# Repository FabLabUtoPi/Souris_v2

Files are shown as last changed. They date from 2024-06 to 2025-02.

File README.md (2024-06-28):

# Souris_v2
Evolution du prototype de souris - Lauréat ANCT
Suite à la réalisation et mis en test des premiers prototypes de la [souris réalisée par le FabLab UtoPi](https://github.com/FabLabUtoPi/Souris) 
Les évolutions suivantes ont été retenues après analyse des retours des utilisateurs/testeurs  

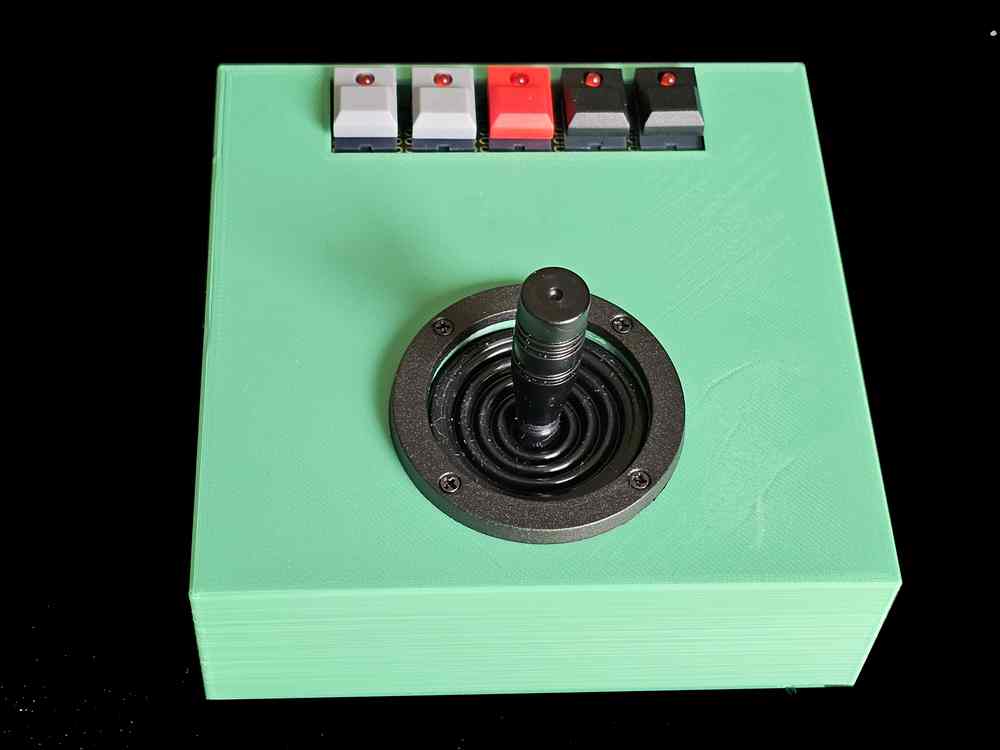
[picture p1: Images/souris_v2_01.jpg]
Image de la souris dans sa deuxième version : boîtier un peu plus grand et joystick analogique.


## Evolutions par rapport au prototype

### Taille du boîtier 
Lors des manipulations du joystick il arrive quel le boîtier se soulève
Deux approches sont possibles : Alourdir le boîtier ou augmenter sa taille 
Le manque de stabilité semble du à la taille du boîtier, la solution retenue  été d'augmenter légèrement la taille du boîtier en conservant le format carré de départ.

### Sensibilité du joystick
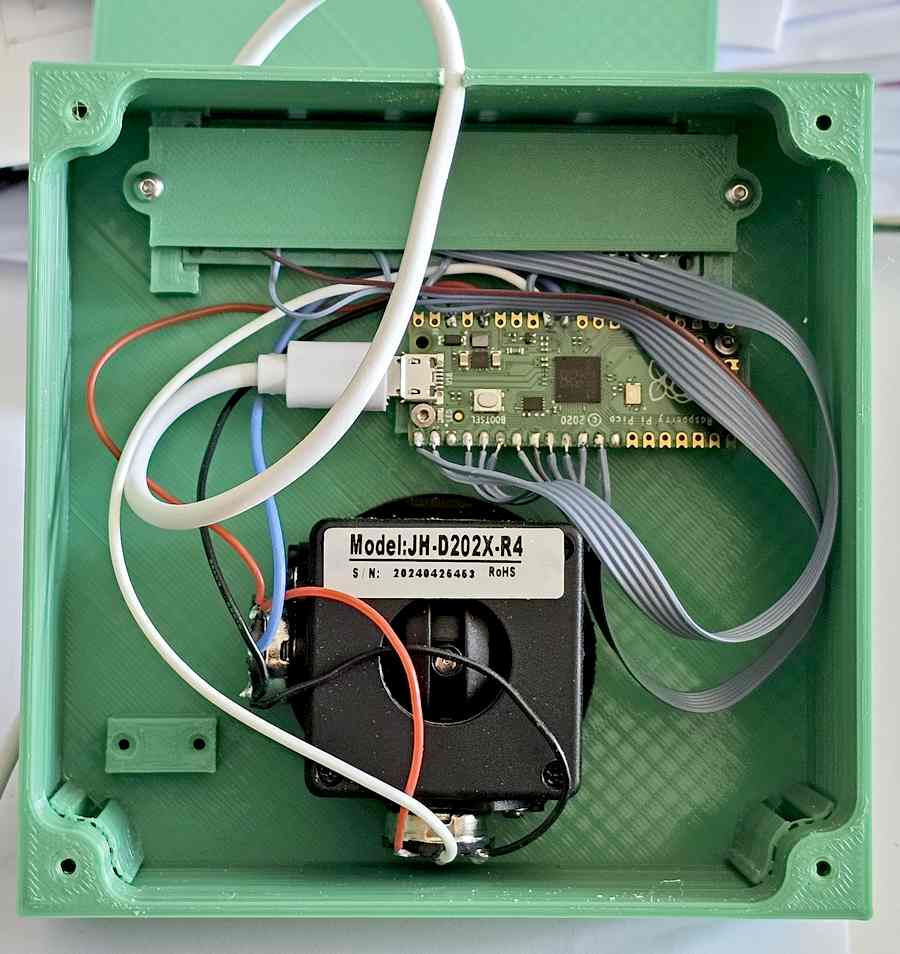
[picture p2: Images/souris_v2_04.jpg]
Image de l'intérieur de la souris dans sa deuxième version : boîtier un peu plus grand et joystick analogique.
  
Le joystick retenu à l'origine est un joystick digital. Les directions de déplacement du curseur de la souris sont commandées par des switchs (des interrupteurs) qui sont activés lorsque l'utilisateur pousse le levier dans une direction. L'accélération de déplacement du curseur est obtenue en maintenant le leviier poussé pendant au moins 0,5 seconde. Si l'utilisateur relache le levier ou change de direction, le déplacement revient en vitesse lente. Il faut de nouveau 0,5 seconde pour accélérer le déplacement. Ceci a conduit à adopter un joystick analogique. le déplacement du levier modifie une tension. En fonction de la position du levier la tension est plus ou moins élevée. Il est possible de définir dans le programme les seuils pour lesquels on passe de la vitesse lente à la vitesse rapide. L'utilisataur peut ainsi doser le déplacement du curseur instantanément, sans devoir respecter un délai.

### Filtrage des mouvements involontaires
La souris peut être utilisée par des personnes présentant des mouvements involontaires (~Parkinson). le joystick analogique permet de filtrer ces mouvements involontaires en filtrant les mouvements pour utiliser une valeur moyenne. 

### Adaptation de la préhension
Le joystick permet de monter un système de préhension adapté à la personne (boule, repose poignet, poignée adaptée après scan de la main)
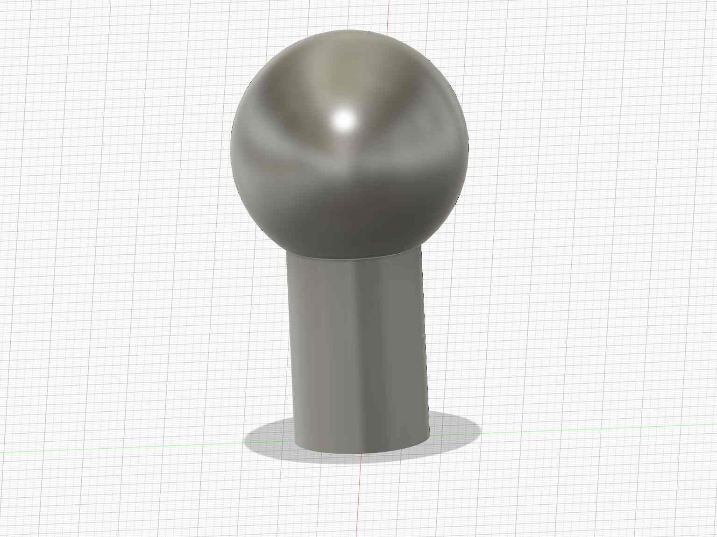
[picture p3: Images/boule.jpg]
Image d'un boule adaptée au joystick analogique.

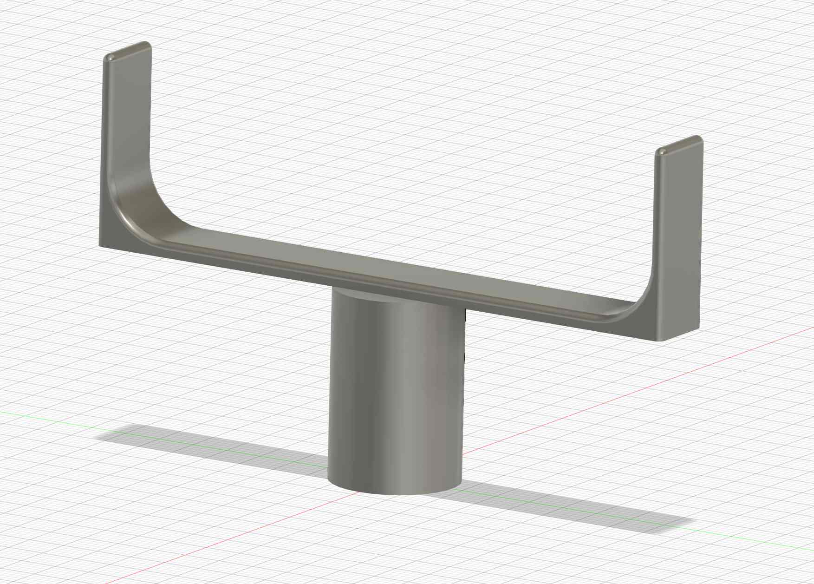
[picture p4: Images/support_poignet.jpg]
Image d'un porte poignet adapté au joystick analogique.


### Réorganisation interne
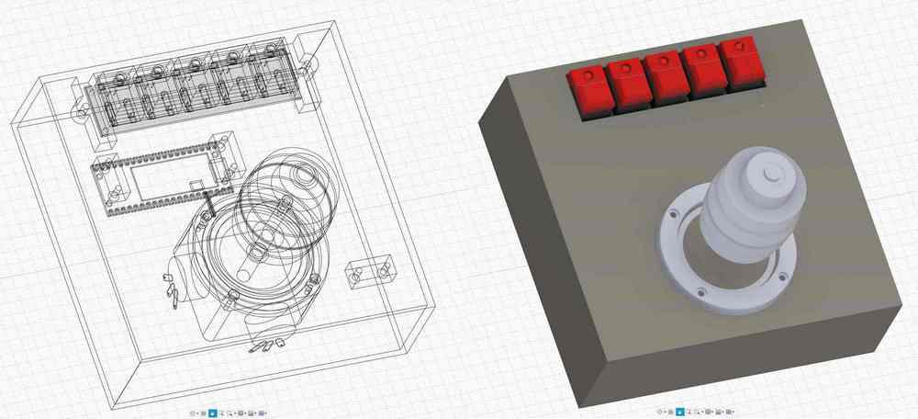
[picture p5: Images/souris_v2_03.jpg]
Image de l'intérieur de la souris dans sa deuxième version : boîtier un peu plus grand et joystick analogique.
  
L'augmentation de la taille du boîtier a permis de placer différemment les composants à l'intérieur du boîtier. Le montage de la souris est facilité et le temps de montage a été réduit de 30% environ

### Fixation de la rampe d'interrupteurs
L'augmentation de taille a également permis de repenser la fixation de la plaquette supportant les interrupteurs avec une meilleure solidité de la fixation et un montage plus rapide.

### Abandon du vibreur
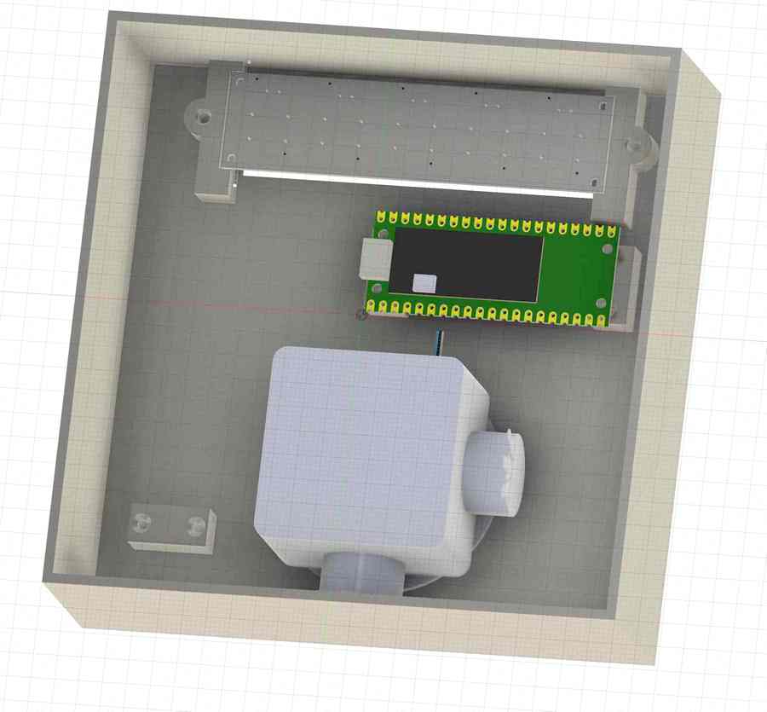
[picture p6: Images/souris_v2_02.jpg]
Image de l'intérieur de la souris dans sa deuxième version : boîtier un peu plus grand et joystick analogique.
  
Pensé pour des non voyants, le premier modèle comportait un buzzer et un vibreur qui fournissait un retour haptique. Il apparait que le buzzer fournit une information suffisante pour un non voyant. Le vibreur a donc été supprimé du schéma mais pourra être ajouté en option pour des personnes mal-entendantes. On garde la possibilité de désactiver le buzzer en appuyant sur une touche au démarrage de la souris.

### Réduction du nombre de pièces à imprimer
La remise en réflexion de la souris et l'augmentation de sa taille ont permis de réduire le nombre de pièces à imprimer à 3 au lieu de 5.

### Augmentation du prix du joystick
Le passage d'un modèle digital (équipé de switchs) à un modèle analogique (équipé de potentiomètres) induit une légère augmentation du coût, le joystick passant de 7€ à 12€ (environ)

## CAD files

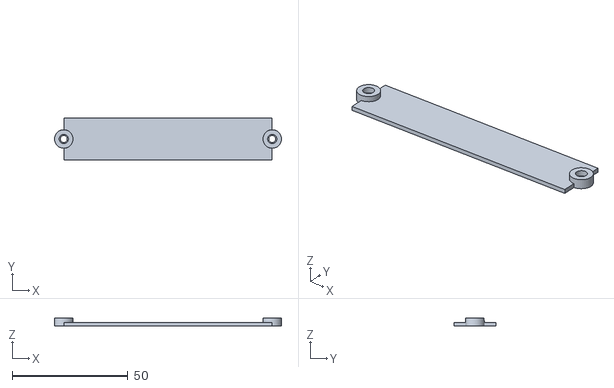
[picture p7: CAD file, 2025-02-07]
Fichiers3D/Souris_ANCT_v2 Plaque fixation BP.stl
98.0 x 18.0 x 3.50

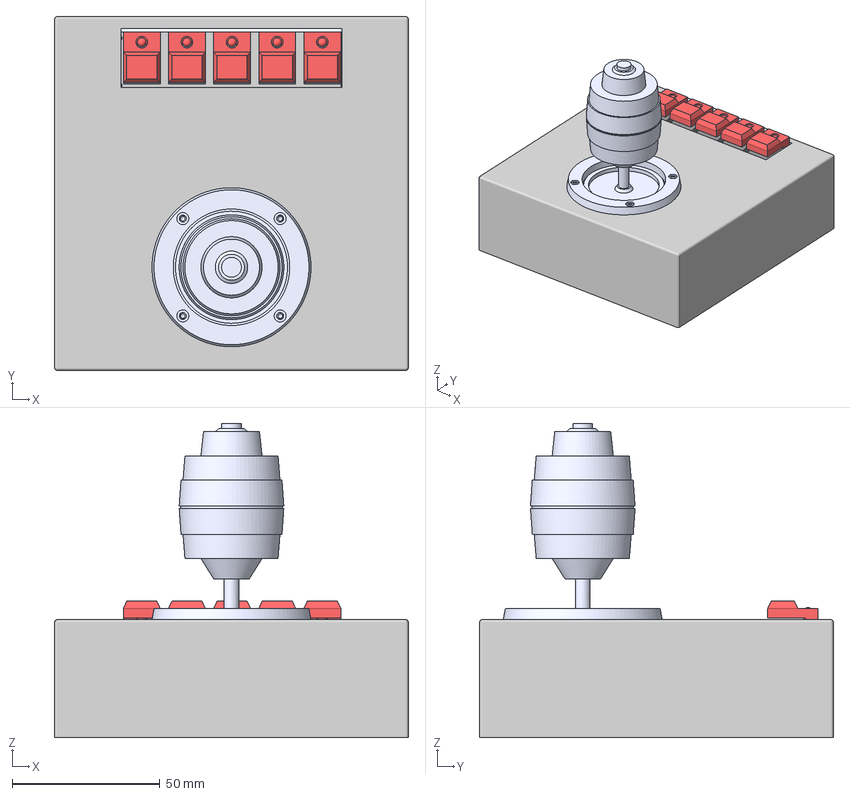
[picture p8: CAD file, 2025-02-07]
Fichiers3D/Souris_ANCT_v2.3mf
120.0 x 120.0 x 106.5 mm
Corps1 x 12
Corps2 x 6
Corps3 x 6
Corps4 x 6
Corps5 x 6
Corps6 x 6
Corps7 x 6
Corps8 x 5
Corps9 x 5

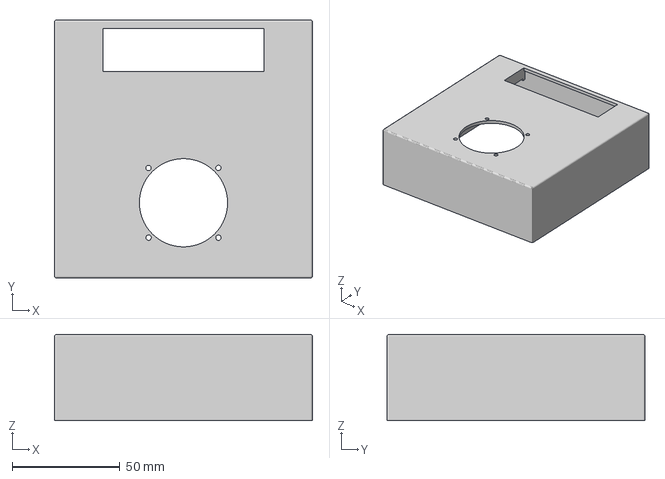
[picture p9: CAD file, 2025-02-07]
Fichiers3D/Souris_ANCT_v2 Boitier.3mf
120.0 x 120.0 x 40.0 mm

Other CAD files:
Fichiers3D/Souris_ANCT_v2 Boitier.stl

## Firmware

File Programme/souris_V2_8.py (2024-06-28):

# Souris pilotee par joystick
# MIT License
# Version 2 avec joystick analogique
# 2 vitesses de déplacement en fonction de la position du joystick
# Avertissement sonore quand deux directions sont activées (diagonale)


# Copyright (c) 2024 FabLabUtoPi

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
# Licence MIT

# Copyright (c) 2024 FabLabUtoPi

# L autorisation est accordée par la présente, gratuitement, à toute personne obtenant une copie de ce
# logiciel et des fichiers de documentation associés (le "Logiciel"), de l'utiliser
# sans restriction, y compris sans limitation d'utilisation, de copie, de modification, de fusion, 
# de publication, de distribution, d'accorder des sous-licences et/ou de vendre des copies du logiciel.
# et/ou de vendre des copies du logiciel, et d'autoriser les personnes à qui le logiciel est fourni
# de le faire, sous réserve des conditions suivantes :

# La licence ci-dessus et cet avis d'autorisation doivent être inclus dans toutes les
# copies ou parties substantielles du logiciel.

# LE LOGICIEL EST FOURNI "EN L'ETAT", SANS GARANTIE D'AUCUNE SORTE, EXPRESSE OU
# EXPLICITE OU IMPLICITE, Y COMPRIS, MAIS SANS S'Y LIMITER, LES GARANTIES DE QUALITÉ MARCHANDE,
# D'ADÉQUATION À UN USAGE PARTICULIER ET D'ABSENCE DE CONTREFAÇON. EN AUCUN CAS LES AUTEURS OU
# LES AUTEURS OU LES DÉTENTEURS DE DROITS D'AUTEUR NE POURRONT ÊTRE TENUS POUR
# RESPONSABLES D'UNE RÉCLAMATION, D'UN DOMMAGE OU D'UNE AUTRE RESPONSABILITÉ, 
# QUE CE SOIT DANS LE CADRE D'UNE ACTION CONTRACTUELLE, DÉLICTUELLE OU AUTRE, DÉCOULANT DE,
# PROVENANT DE OU EN RELATION AVEC LE LOGICIEL OU AVEC SON UTILISATION 
# OU D'AUTRES TRANSACTIONS LIEES AU LOGICIEL.


# Références
# Source https://docs.circuitpython.org/projects/hid/en/latest/_modules/adafruit_hid/mouse.html
# https://docs.circuitpython.org/projects/hid/en/latest/api.html#adafruit_hid.mouse.Mouse
#
# Créé par le FabLab UtoPi Le Creusot
# Contact : contact@fablab-utopi.org 
# La position x=0, y=0 pour la souris est en haut à gauche de l'écran
#
# COnnexion des potentiomètres
# Horizontal           Déplacement droite-gauche     A1
# Vertical             Déplacement Haut-Bas          A0

# Connexion des switchs
# Peut se modifier en fonction de vos connexions

# GAUCHE               Appui bouton gauche souris    GP5
# DROITE               Appui bouton droit souris     GP6

# PROG                 Lancement programme           GP7

# Wheel UP             Roulette vers le haut         GP8
# Wheel DOWN           Roulette vers le bas          GP9

# Connexion des LEDs
# DROITE               LED Bouton droit              GP0
# GAUCHE               LED Bouton gauche             GP1
# PROG                 LED Lancement programme       GP2
# Wheel UP             LED Roulette vers le haut     GP3
# Wheel DOWN           LED Roulette vers le bas      GP4

# Vibreur  NON CONNECTE                              GP14
# Buzzer                                             GP15

# Importation des bibliotheques utilisées
import time
import analogio
import board
import digitalio
import usb_hid
import array
import pulseio
from adafruit_hid.mouse import Mouse
from adafruit_hid.keyboard import Keyboard
from adafruit_hid.keycode import Keycode

mouse = Mouse(usb_hid.devices)

kbd = Keyboard(usb_hid.devices)

x_axis = analogio.AnalogIn(board.A1)
y_axis = analogio.AnalogIn(board.A0)

pot_min = 0.00
pot_max = 3.29
step = (pot_max - pot_min) / 20.0

def get_voltage(pin):
    return (pin.value * 3.3) / 65536

def steps(axis):
    return round((axis - pot_min) / step)

# Définir la LED interne au Raspberry Pi PICO
led = digitalio.DigitalInOut(board.GP25)
led.direction = digitalio.Direction.OUTPUT
# Eteindre la LED du Raspberry Pi PICO
led.value = 0

# Définir les LED des boutons poussoir
led1 = digitalio.DigitalInOut(board.GP0)
led1.direction = digitalio.Direction.OUTPUT

led1.value = 0

led2 = digitalio.DigitalInOut(board.GP1)
led2.direction = digitalio.Direction.OUTPUT
# Eteindre la LED2
led2.value = 0

led3 = digitalio.DigitalInOut(board.GP2)
led3.direction = digitalio.Direction.OUTPUT
# Eteindre la LED3
led3.value = 0

led4 = digitalio.DigitalInOut(board.GP3)
led4.direction = digitalio.Direction.OUTPUT
# Eteindre la LED4
led4.value = 0

led5 = digitalio.DigitalInOut(board.GP4)
led5.direction = digitalio.Direction.OUTPUT
# Eteindre la LED5
led5.value = 0

# Definir les boutons poussoirs de la souris
# De gauche à droite :
# Clic gauche, clic droit, programme, roulette up, roulette down
# Clic gauche / Appui sur Joystick
LEFT_BUTTON = digitalio.DigitalInOut(board.GP9)
LEFT_BUTTON.direction = digitalio.Direction.INPUT
LEFT_BUTTON.pull = digitalio.Pull.UP

# Clic droit
RIGHT_BUTTON = digitalio.DigitalInOut(board.GP8)
RIGHT_BUTTON.direction = digitalio.Direction.INPUT
RIGHT_BUTTON.pull = digitalio.Pull.UP
# 
# Bouton PROG
PROG_BUTTON = digitalio.DigitalInOut(board.GP7)
PROG_BUTTON.direction = digitalio.Direction.INPUT
PROG_BUTTON.pull = digitalio.Pull.UP

# Roulette UP
up = digitalio.DigitalInOut(board.GP6)
up.direction = digitalio.Direction.INPUT
up.pull = digitalio.Pull.UP

# Roulette DOWN
down = digitalio.DigitalInOut(board.GP5)
down.direction = digitalio.Direction.INPUT
down.pull = digitalio.Pull.UP

# Définir les directions du joystick
dir_G = False
dir_D = False
dir_H = False
dir_B = False

# Faire Flasher la LED de la carte PICO
def blink():
    led.value = 1
    time.sleep(0.05)
    led.value = 0

# Clignoter pour montrer que le programme demarre
# vu uniquement sur le Raspberry Pi PICO
for i in range(0, 5):
    blink()
    time.sleep(0.02)

# Declarer le Vibreur - Inutilise en V2
# vibreur = digitalio.DigitalInOut(board.GP14)
# vibreur.direction = digitalio.Direction.OUTPUT

# Declarer le Buzzer
buzzer = pulseio.PulseOut(board.GP15, frequency=3000, duty_cycle=32768)
pulses = array.array('H', [65000, 1000, 65000, 65000, 1000])


# Chenillard des LEDs avant de démarrer
# Utile pour la mise au point
#   et la verification du bon fonctionnement du programme
led1.value = True
time.sleep(0.05)
led2.value = True
time.sleep(0.05)
led3.value = True
time.sleep(0.05)
led4.value = True
time.sleep(0.05)
led5.value = True
time.sleep(0.4)
led5.value = False
time.sleep(0.05)
led4.value = False
time.sleep(0.05)
led3.value = False
time.sleep(0.05)
led2.value = False
time.sleep(0.05)
led1.value = False
time.sleep(0.05)

# Définir les valeurs de déplacement du curseur sur l'écran
# Nombre de pixels dont le curseur se déplace
v_lent = 8
v_rapide = 16

# Définir la durée de la temporisation de boucle principale
# 0,05 seconde par défaut
tempo_boucle = 0.05

# Définir l'intervalle de temps entre les bips quand on déplace en diagonale
# 1 seconde par défaut
tempo_bip = 1

# Démarrer le chronométrage pour le BIP
# Le bip est activé toutes les secondes si le curseur se déplace en diagonale
t_debut = time.monotonic()

# Mettre le flag du BIP à 0
flag_BIP = 0

# Test vibreur - Pas utilise dans cette version
# vibreur.value = True
# time.sleep(0.1)
# vibreur.value = False
# time.sleep(0.5)

# Test buzzer
buzzer.send(pulses)

# Allumer LED 1 utilisé pour les test
def led1_on():
    led1.value = 1
    time.sleep(0.05)
    led1.value = 0

# Fermer la fenetre CIRCUITPI qui s ouvre a  la connexion
# Mettre en commentaire pendant les essais sinon l editeur se ferme !
# kbd.send(Keycode.LEFT_ALT, Keycode.F4)

# BOUCLE PRINCIPALE DU PROGRAMME ===============
while True:
    try:
        # Déplacer le curseur en fonction de la positions du joystick
        x = get_voltage(x_axis)
        y = get_voltage(y_axis)
        print(steps(x))
        print(steps(y))

        if steps(x) > 12.0:
            dir_D = True
            # print(steps(x))
            mouse.move(x = v_lent)
        if steps(x) < 8.0:
            dir_G = True
            # print(steps(x))
            mouse.move(x = -v_lent)

        if steps(x) > 16.0:
            dir_D = True
            # print(steps(x))
            mouse.move(x = v_rapide)
        if steps(x) < 4.0:
            dir_G = True
            # print(steps(x))
            mouse.move(x = -v_rapide)

        if steps(y) > 12.0:
            dir_H = True
            # print(steps(y))
            mouse.move(y = -v_lent)
        if steps(y) < 8.0:
            dir_B = True
            # print(steps(y))
            mouse.move(y = v_lent)

        if steps(y) > 16.0:
            dir_H = True
            # print(steps(y))
            mouse.move(y = -v_rapide)
        if steps(y) < 4.0:
            dir_B = True
            # print(steps(y))
            mouse.move(y = v_rapide)

        # Si on active 2 directions simultanement
        # Actionner le buzzer au maxi une fois par seconde
        if ((dir_G and dir_H) or (dir_D and dir_H) or (dir_G and dir_B) or (dir_D and dir_B)) == True :
            # On est en diagonale mettre le flag_BIP à 1
            flag_BIP = 1
            # Si le flag est à 0, on n'a pas encore bippé
            if flag_BIP == 1:
                # Est ce qu'il s'est écoulé une seconde depuis le dernier bip ?
                if (time.monotonic() - t_debut) > tempo_bip:
                    print("BIP ! Flag à 1 Temps = ", time.monotonic())
                    buzzer.send(pulses)
                    led1_on()
                    t_debut = time.monotonic()
                else:
                    # Le flag est à 0 et on est passé en diagonale = on bippe
                    flag_BIP = 1
        else:
            # On n'est plus en diagonale : enlever le flag
            flag_BIP = 0
        
        # Remettre la direction au centre pour la prochaine lecture
        dir_G = False
        dir_D = False
        dir_H = False
        dir_B = False
        

        # Bouton gauche de la souris
        if (LEFT_BUTTON.value is False):
            # Si un bouton est appuye on positionne le flag
            flag = 1
            print("BOUTON GAUCHE valeur = ", LEFT_BUTTON.value)
            mouse.click(Mouse.LEFT_BUTTON)
            led1.value = True
        else:
            led1.value = False

        # Bouton droit de la souris
        if (RIGHT_BUTTON.value is False):
            # Si un bouton est appuye on positionne le flag
            flag = 1
            print("BOUTON DROIT valeur = ", RIGHT_BUTTON.value)
            mouse.click(Mouse.RIGHT_BUTTON)
            led2.value = True
        else:
            led2.value = False

        # Bouton PROGRAMMABLE de la souris
        if (PROG_BUTTON.value is False):
            # Si un bouton est appuye on positionne le flag
            flag = 1
            print("BOUTON CENTRAL valeur = ", PROG_BUTTON.value)
            buzzer.send(pulses)
            # Envoyer code clavier
            kbd.press(Keycode.WINDOWS)
            time.sleep(.09)
            kbd.release(Keycode.WINDOWS)
            led3.value = True
        else:
            led3.value = False

        # Roulette haut
        if (up.value is False):
            # Si un bouton est appuye on positionne le flag
            flag = 1
            print("Roulette UP valeur = ", up.value)
            mouse.move(wheel=1)
            led4.value = True
        else:
            led4.value = False

        # Roulette bas
        if (down.value is False):
            # Si un bouton est appuyé on positionne le flag
            flag = 1
            print("Roulette DOWN valeur = ", down.value)
            mouse.move(wheel=-1)
            led5.value = True
        else:
            led5.value = False

        # Tempo de la boucle de lecture des boutons
        time.sleep(tempo_boucle)
    except KeyboardInterrupt:
        raise Exception("Arrete par l utilisateur")
